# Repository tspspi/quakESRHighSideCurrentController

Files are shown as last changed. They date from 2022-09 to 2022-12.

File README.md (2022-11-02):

# Simple 500 mA high voltage biasable current source

This project contains a simple OpAmp and MosFET based current supply
that can be controlled using a serial port. The whole project is built
around an ```IRF540N``` MosFET that's driven by an ```LM358``` OpAmp in a way
to keep the voltage drop over a sense resistor constant - thus it provides
a controllable current source (note that there is no temperature compensation
but that was not necessary for this application).

The reference voltage is provided by an ```MCP4822``` SPI digital to analog
converter that's controlled by an ```ATMega328P```. The serial port that's used
to control the current source is isolated using two ```PC816``` optocouplers - this
is necessary since the whole board will be biased to ```-2 kV``` with respect to the
controlling system. The load is powered by an 12V isolation transformer, the controller
uses the same power supply and derives it's 5V supply for DAC and microcontroller using
a simple ```LM317``` linear voltage regulator.

## The schematic

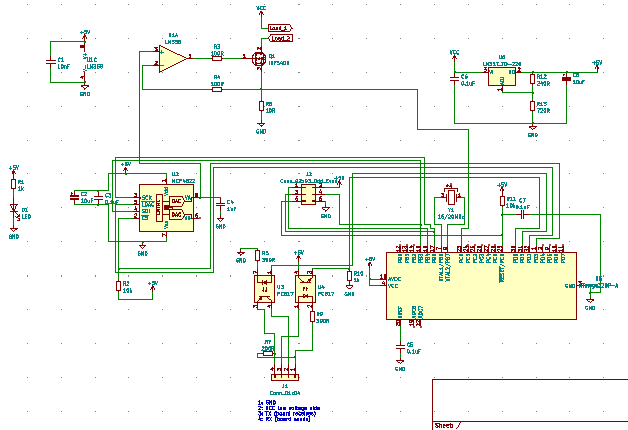
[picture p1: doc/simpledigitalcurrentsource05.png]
The schematic


The schematic can be found in KiCAD format in the ```/kicad/currentcontroller``` directory

## A PCB design

This repository includes also a simple PCB design

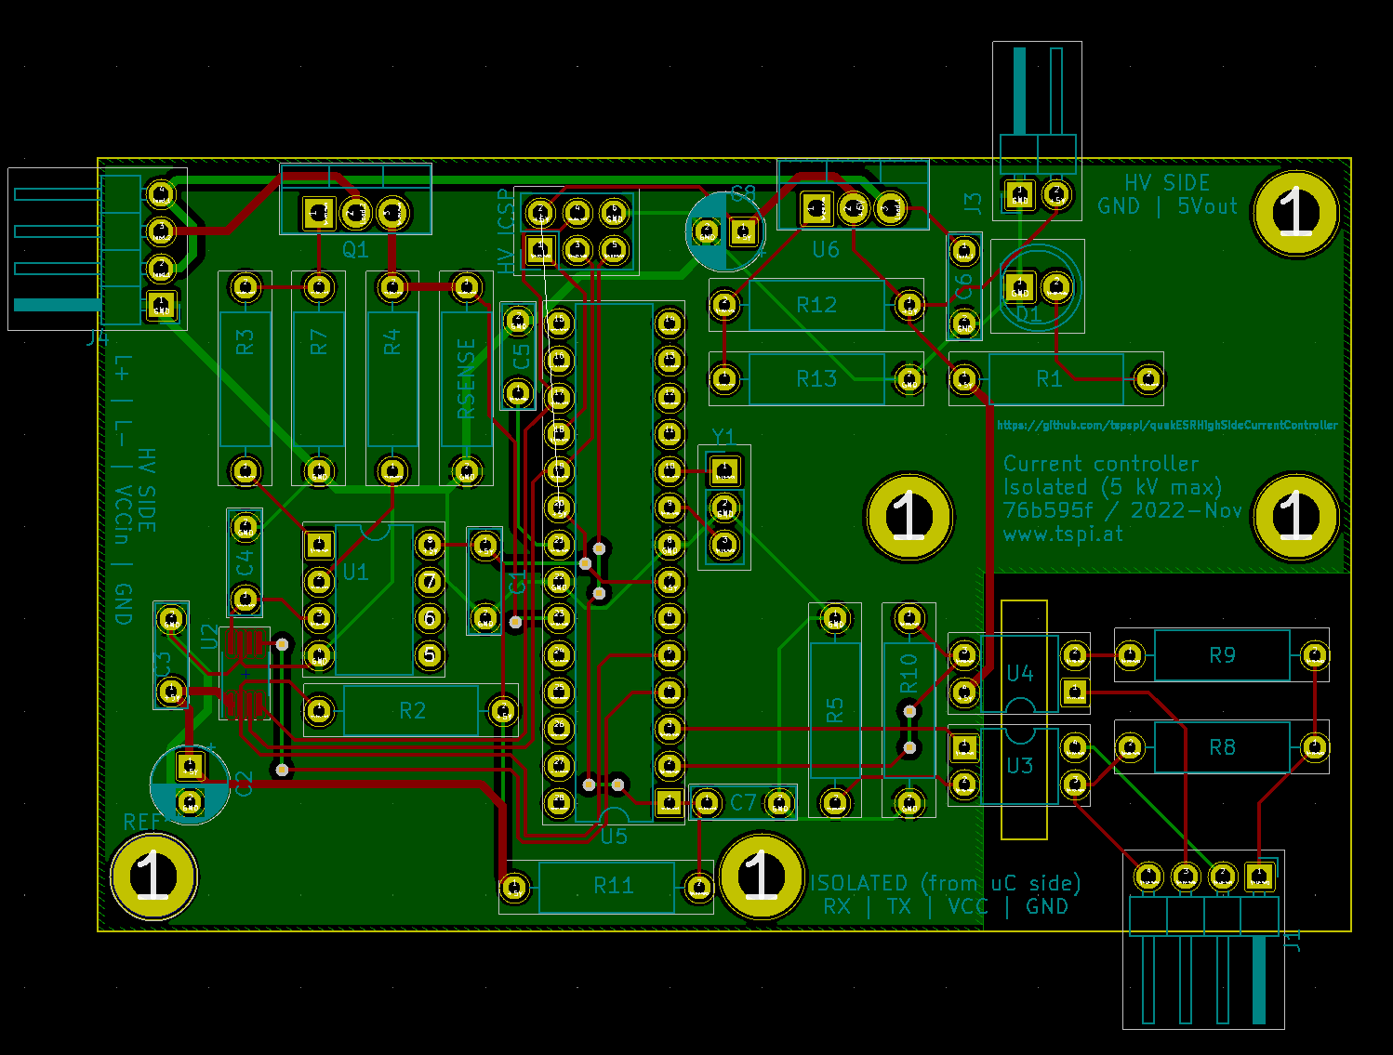
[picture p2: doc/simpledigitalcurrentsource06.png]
PCB design


## Microcontroller firmware

The firmware for the microcontroller can be found in ```mcusrc``` and is built
using ```avr-gcc```. The firmware can be flashed by using the ```Makefile```:

```
make flash
```

The ACSL annotations are work in progress.

## Test script

To test the communication using a [simple serial TTL to USB converter](https://amzn.to/3C0tQMZ)
a simple Python library is available (currently no PyPi package) at ```mcusrc/sertest```

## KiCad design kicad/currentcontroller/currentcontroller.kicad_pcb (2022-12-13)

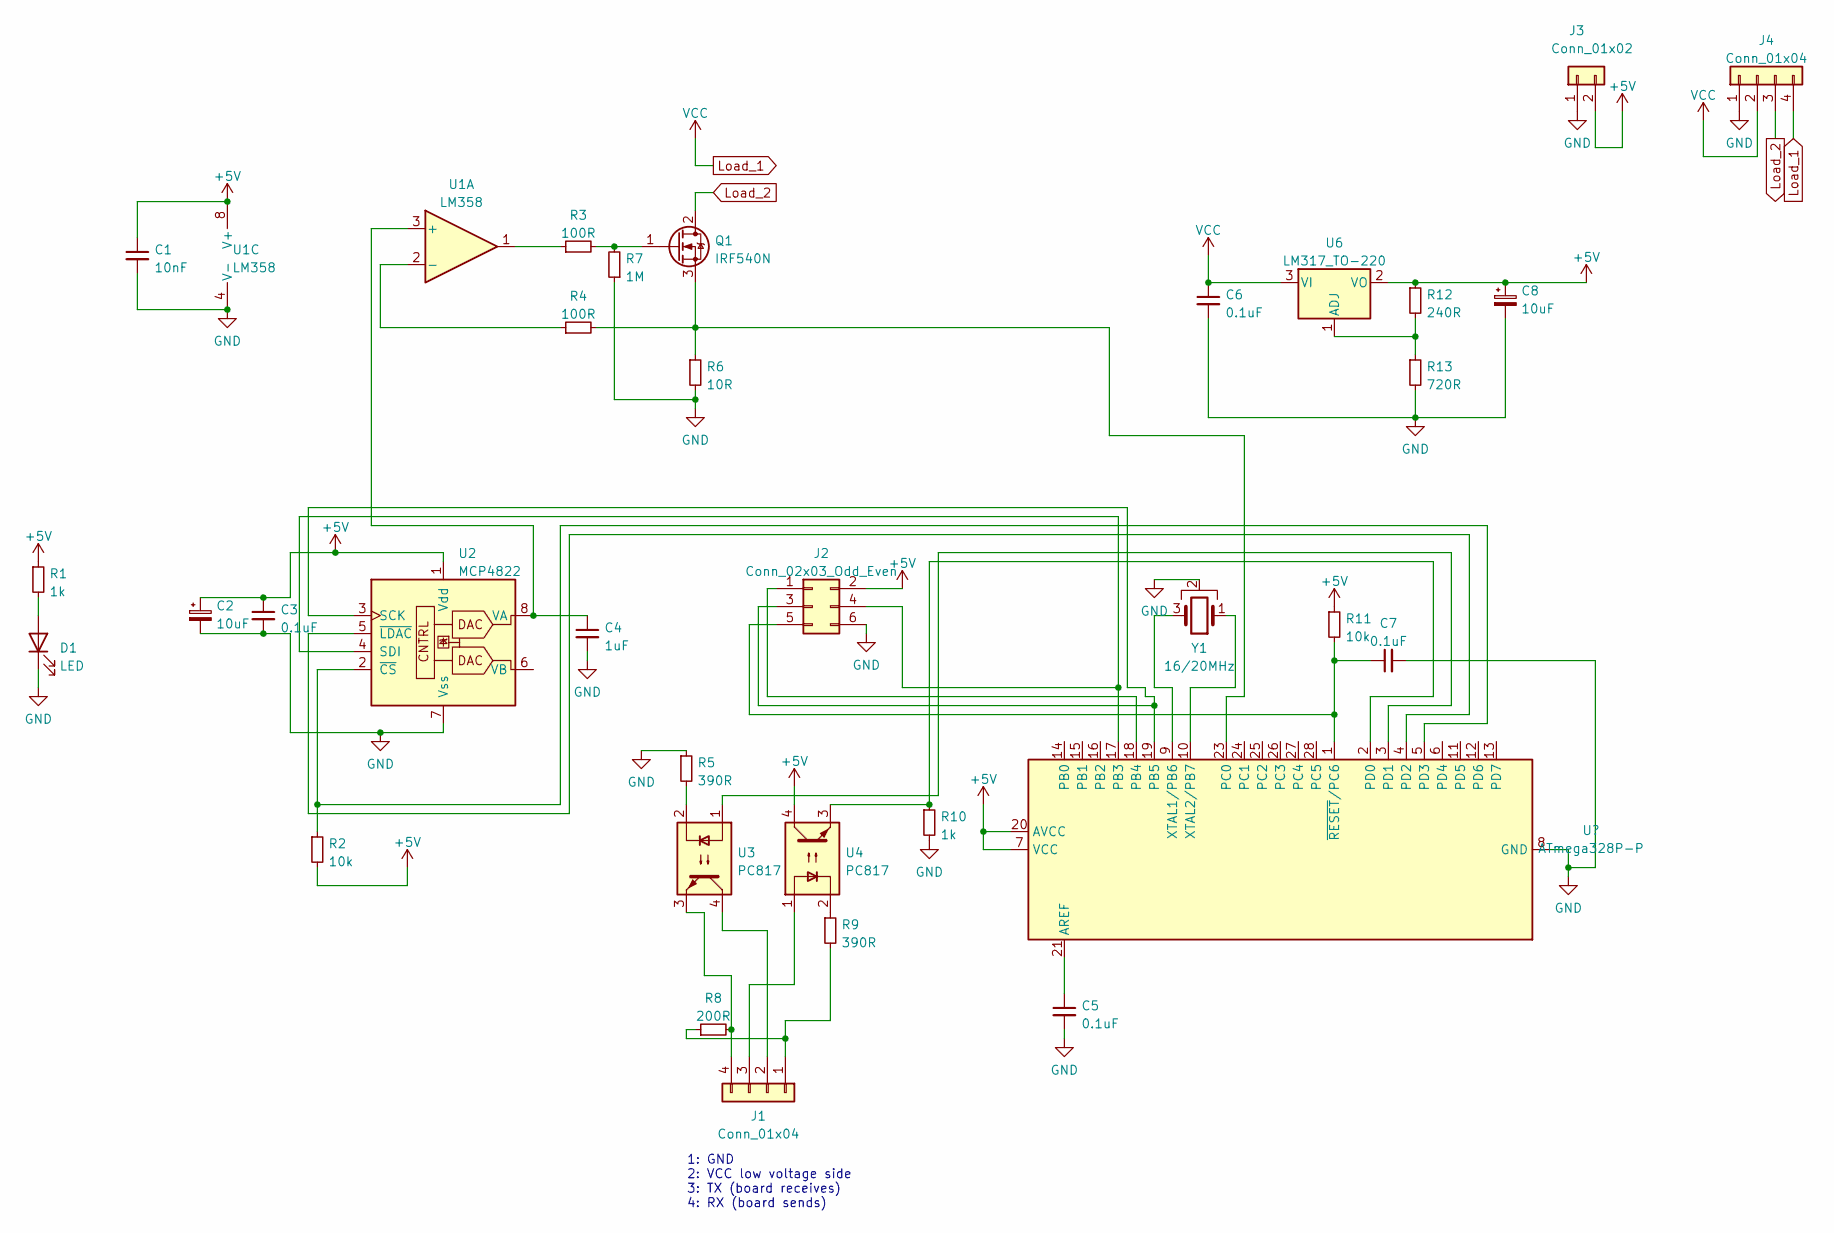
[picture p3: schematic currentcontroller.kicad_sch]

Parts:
C1: 10nF; C_Rect_L7.0mm_W2.0mm_P5.00mm
C2, C8: 10uF; CP_Radial_D5.0mm_P2.50mm
C3, C5, C6, C7: 0.1uF; C_Rect_L7.0mm_W2.0mm_P5.00mm
C4: 1uF; C_Rect_L7.0mm_W2.0mm_P5.00mm
D1: LED; LED_D5.0mm
J1, J4: Conn_01x04; PinHeader_1x04_P2.54mm_Horizontal
J2: Conn_02x03_Odd_Even; PinHeader_2x03_P2.54mm_Vertical
J3: Conn_01x02; PinHeader_1x02_P2.54mm_Horizontal
Q1: IRF540N; TO-220-3_Vertical
R1, R10: 1k; R_Axial_DIN0309_L9.0mm_D3.2mm_P12.70mm_Horizontal
R2, R11: 10k; R_Axial_DIN0309_L9.0mm_D3.2mm_P12.70mm_Horizontal
R3, R4: 100R; R_Axial_DIN0309_L9.0mm_D3.2mm_P12.70mm_Horizontal
R5, R9: 390R; R_Axial_DIN0309_L9.0mm_D3.2mm_P12.70mm_Horizontal
R6: 10R; R_Axial_DIN0309_L9.0mm_D3.2mm_P12.70mm_Horizontal
R7: 1M; R_Axial_DIN0309_L9.0mm_D3.2mm_P12.70mm_Horizontal
R8: 200R; R_Axial_DIN0309_L9.0mm_D3.2mm_P12.70mm_Horizontal
R12: 240R; R_Axial_DIN0309_L9.0mm_D3.2mm_P12.70mm_Horizontal
R13: 720R; R_Axial_DIN0309_L9.0mm_D3.2mm_P12.70mm_Horizontal
U1: LM358; DIP-8_W7.62mm
U2: MCP4822; MSOP-8_3x3mm_P0.65mm
U3, U4: PC817; DIP-4_W7.62mm
U6: LM317_TO-220; TO-220-3_Vertical
Y1: 16/20MHz; PinHeader_1x03_P2.54mm_Vertical

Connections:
+5V: C1.1, C2.1, C3.1, C8.1, J2.2, J3.2, R1.1, R2.2, R11.1, R12.1, U1.8 (V+), U2.1 (Vdd), U4.4, U6.2 (VO); also elsewhere on the board
GND: C1.2, C2.2, C3.2, C4.2, C5.2, C6.2, C7.2, C8.2, D1.1 (K), J2.6, J3.1, J4.1, R5.1, R6.2, R7.1, R10.2, R13.2, U1.4 (V-), U2.7 (Vss), Y1.2; also elsewhere on the board
Load_1: C6.1, J4.2, J4.4, U6.3 (VI)
Load_2: J4.3, Q1.2 (D)
unnamed: C4.1, U1.3 (+), U2.8 (VA)
unnamed 5: C5.1; also elsewhere on the board
unnamed 6: C7.1, J2.5, R11.2; also elsewhere on the board
unnamed: D1.2 (A), R1.2
unnamed: J1.1, R8.1, R9.2
unnamed: J1.2, U3.4
unnamed: J1.3, U4.1
unnamed: J1.4, R8.2, U3.3
unnamed 13: J2.3, U2.3 (SCK); also elsewhere on the board
unnamed 14: J2.4, U2.4 (SDI); also elsewhere on the board
unnamed: Q1.1 (G), R3.2, R7.2
unnamed 16: Q1.3 (S), R4.2, R6.1; also elsewhere on the board
unnamed 17: R2.1, U2.2 (~CS); also elsewhere on the board
unnamed: R3.1, U1.1
unnamed: R4.1, U1.2 (-)
unnamed: R5.2, U3.2
unnamed: R9.1, U4.2
unnamed 22: R10.1, U4.3; also elsewhere on the board
unnamed: R12.2, R13.1, U6.1 (ADJ)
unnamed 24: U2.5 (~LDAC); also elsewhere on the board
unnamed 25: U3.1; also elsewhere on the board
unnamed 26: Y1.1; also elsewhere on the board
unnamed 27: Y1.3; also elsewhere on the board

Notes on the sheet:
1: GND 2: VCC low voltage side 3: TX (board receives) 4: RX (board sends)

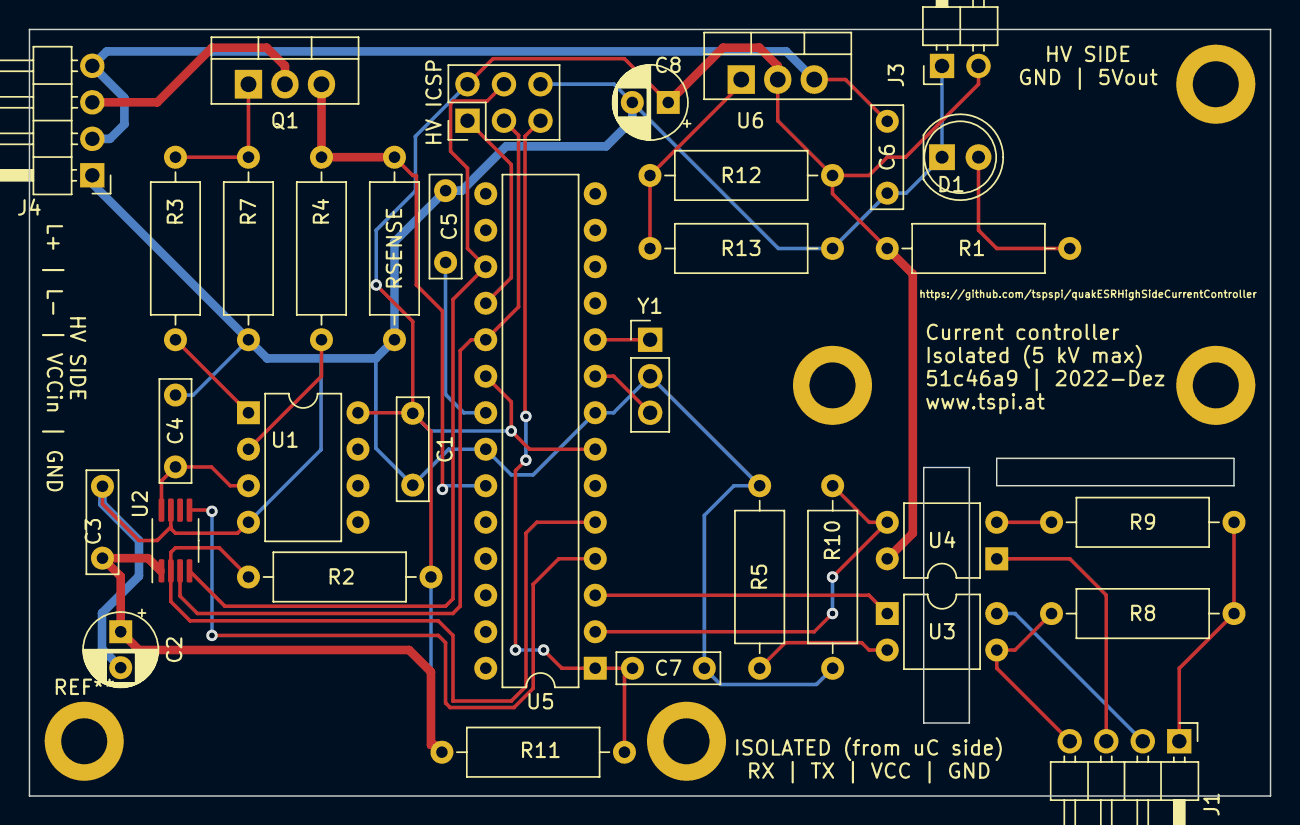
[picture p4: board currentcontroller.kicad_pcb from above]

Board: 2 copper layers, 86.4 x 53.3 mm, 34 parts (0 on the bottom side), 28 nets.

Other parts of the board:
HV ICSP: Conn_02x03_Odd_Even; PinHeader_2x03_P2.54mm_Vertical
RSENSE: 10R; R_Axial_DIN0309_L9.0mm_D3.2mm_P12.70mm_Horizontal
U5: ATmega328P-P; DIP-28_W7.62mm

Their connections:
+5V: HV ICSP.2, U5.7 (VCC), U5.20 (AVCC); also elsewhere on the board
GND: HV ICSP.6, RSENSE.2, U5.8 (GND), U5.22 (GND); also elsewhere on the board
unnamed 5: U5.21 (AREF); also elsewhere on the board
unnamed 6: HV ICSP.5, U5.1 (~RESET/PC6); also elsewhere on the board
unnamed: HV ICSP.1, U5.18 (PB4)
unnamed 13: HV ICSP.3, U5.19 (PB5); also elsewhere on the board
unnamed 14: HV ICSP.4, U5.17 (PB3); also elsewhere on the board
unnamed 16: RSENSE.1, U5.23 (PC0); also elsewhere on the board
unnamed 17: U5.5 (PD3); also elsewhere on the board
unnamed 22: U5.2 (PD0); also elsewhere on the board
unnamed 24: U5.4 (PD2); also elsewhere on the board
unnamed 25: U5.3 (PD1); also elsewhere on the board
unnamed 26: U5.10 (XTAL2/PB7); also elsewhere on the board
unnamed 27: U5.9 (XTAL1/PB6); also elsewhere on the board

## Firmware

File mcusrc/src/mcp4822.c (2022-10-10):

#define __is_in_module__142e0c51_431e_11ed_9e74_b499badf00a1 1

#include <avr/io.h>
#include <avr/interrupt.h>
#include <math.h>

#include "main.h"
#include "mcp4822.h"

#ifdef __cplusplus
	extern "C" {
#endif

uint16_t mcp4822_CurrentValues[2] = { 0, 0 };

/*@
	requires \valid(&SPCR) && \valid(&SPSR) && \valid(&PORTD);

	assigns PORTD;
	assigns SPCR;
	assigns SPSR;

	ensures (PORTD & 0x08) == 0;
	ensures SPCR == 0x53;
	ensures SPSR == 0x01;
*/
static inline void mcp4822SPI_TransferBegin() {
	SPCR = 0x50 | 0x03;
	SPSR = 0x01;

	/* Chip select to low ... */
	PORTD = PORTD & (~(0x08));
}
/*@
	requires \valid(&SPCR) && \valid(&PORTD);

	assigns PORTD;
	assigns SPCR;

	ensures (PORTD & 0x08) == 0x08;
	ensures SPCR == 0x40;
*/
static inline void mcp4822SPI_TransferEnd() {
	SPCR = 0x40;
	PORTD = PORTD | 0x08;
}
/*@
	requires \valid(&SPDR) && \valid(&SPSR);

	assigns SPDR;

	ensures \result == SPDR;
*/
static inline uint8_t mcp4822SPI_Transfer(uint8_t byteOut) {
	SPDR = byteOut;
	asm volatile("nop");
	while((SPSR & 0x80) == 0) { }
	return SPDR;
}
/*@
	requires \valid(&PORTD);

	assigns PORTD;

	ensures (PORTD & 0x04) == 0x04;
*/
static inline void mcp4822SPI_LatchOutputs() {
	PORTD = PORTD & (~0x04);
	/* Two NOPs to reach 100 ns minimum time (at 16 MHz each is ~ 62 ns) */
	//@ assert (PORTD & 0x04) == 0;
	asm volatile("nop");
	asm volatile("nop");
	PORTD = PORTD | 0x04;
}

/*@
	requires \valid(&SREG) && \valid(&DDRD) && \valid(&PORTD) && \valid(&DDRB) && \valid(&SPCR) && \valid(&SPSR);

	assigns SREG;
	assigns DDRD, PORTD;
	assigns DDRB;
	assigns SPCR, SPSR;
	assigns PRR;

	ensures (DDRD & 0x0C) == 0x0C;
	ensures (PORTD & 0x0C) == 0x0C;
	ensures ((DDRB & 0x24) == 0x24) && ((DDRB & 0x10) == 0);
	ensures (SPCR = 0x40) && (SPSR == 0x01);
	ensures SREG == \old(SREG);
	ensures PRR & 0x04 == 0x00;
*/
void mcp4822Init() {
	uint8_t sregOld = SREG;
	#ifndef FRAMAC_SKIP
		cli();
	#endif

	/*
		Set I/O pins for SPI
			PD3 -> nCS
			PD2 -> nLDAC
			PB5 -> SCK
			PB3 -> SDI (MOSI)
			PB4 -> MISO

			PB2 is slave select, should be configured as output

		nCS -> output, high
		nLDAC -> output, high

	*/
	DDRD = DDRD | 0x0C;
	PORTD = PORTD | 0x0C;
	DDRB = (DDRB | 0x2C) & (~(0x10));
	PORTB = PORTB | 0x2C;

	/* Disable power saving mode ... */
	PRR = PRR & ~(0x04);

	/* SPI master mode, enable logic */
	SPCR = 0x40;
	SPSR = 0x01;

	SREG = sregOld;

	/* Set our output values to 0 */
	mcp4822SetOutput(0, 0, false, 0);
	mcp4822SetOutput(1, 0, false, 0);
}

/*@
	requires (channel == 1) || (channel == 0);
	requires (gain == 1) || (gain == 0);
	requires (enableOutput == true) || (enableOutput == false);
	requires (value > 0) && (value < 4096);

	assigns SPSR, SPCR, SPDR;
	assigns mcp4822_CurrentValues[0], mcp4822_CurrentValues[1];

	ensures mcp4822_CurrentValues[channel] == value;
*/
void mcp4822SetOutput(
	uint8_t channel,
	uint8_t gain,
	bool enableOutput,
	uint16_t value
) {
	uint16_t msg = 0x00;

	/* Prepare message */
	msg = (value & 0x0FFF);
	if(channel != 0) {
		msg = msg | 0x8000;
	}
	if(gain != 0) {
		msg = msg | 0x2000;
	}
	if(enableOutput == true) {
		msg = msg | 0x1000;
	}

	/* Transmit 2 bytes ...*/
	mcp4822SPI_TransferBegin();
	mcp4822SPI_Transfer((uint8_t)((msg & 0xFF00) >> 8));
	mcp4822SPI_Transfer((uint8_t)(msg & 0x00FF));
	mcp4822SPI_TransferEnd();
	mcp4822SPI_LatchOutputs();

	mcp4822_CurrentValues[channel] = value;
}

#ifdef __cplusplus
	} /* extern "C" { */
#endif

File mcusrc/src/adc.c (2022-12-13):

#include <avr/io.h>
#include <avr/interrupt.h>
#include <avr/eeprom.h>
#include <math.h>
#include <util/twi.h>
#include <stdint.h>

#define CURRENT_MEASURE_ADC 0

#include "./adc.h"
#include "./main.h"

#ifdef __cplusplus
    extern "C" {
#endif

uint16_t currentADC[ADCCOUNT];

static double adcCal_K, adcCal_D;
static uint16_t adcCalLow_Counts;
static uint16_t adcCalHigh_Counts;
static uint16_t adcCalHigh_Milliamps;

/*@
	requires \valid(&ADC) && \valid(&ADMUX);

	assigns currentADC[0 .. ADCCOUNT];
*/
ISR(ADC_vect) {
	uint8_t oldMUX = ADMUX;
    currentADC[(oldMUX + (ADCCOUNT-1)) % ADCCOUNT] = ADC;
    ADMUX = (((oldMUX & 0x1F) + 1) % ADCCOUNT) | (oldMUX & 0xE0);
}

struct eepromCalData {
    double adc0_K;
    double adc0_D;

    uint8_t chkSum;
};

/*@
	requires \valid(&ADMUX) && \valid(&ADCSRB) && \valid(&ADCSRA) && \valid(&SREG);

    assigns ADMUX;
    assigns ADCSRB;
    assigns ADCSRA;
    assigns SREG;

    ensures (ADMUX == 0x40);
    ensures (ADCSRB == 0x00);
    ensures ADCSRA == 0xFF;
	ensures SREG == \old(SREG);
*/
void adcInit() {
    unsigned long int i;
    struct eepromCalData calData;

    uint8_t oldSREG = SREG;
    #ifndef FRAMAC_SKIP
        cli();
    #endif

    for(i = 0; i < sizeof(currentADC) / sizeof(uint16_t); i=i+1) {
        currentADC[i] = ~0;
    }

    ADMUX = 0x40; /* AVCC reference voltage, MUX 0, right aligned */
    ADCSRB = 0x00; /* Free running trigger mode, highest mux bit 0 */
    ADCSRA = 0xBF; /* Prescaler / 128 -> about 1 kHz measurement interrupt enable; ADCs currently DISABLED */

    SREG = oldSREG;

    /* Launch ADC ... */
    ADCSRA = ADCSRA | 0x40; /* Start first conversion ... */

    /*
        Load calibration data (if exists)...
    */
    eeprom_read_block(&calData, EEPROM_ADCCALDATAOFFSET, sizeof(struct eepromCalData));
    uint8_t chkSum = 0;
    for(i = 0; i < sizeof(struct eepromCalData); i=i+1) {
        chkSum = chkSum ^ ((uint8_t*)(&calData))[i];
    }
    if(chkSum == 0) {
        adcCal_D = calData.adc0_D;
        adcCal_K = calData.adc0_K;
    } else {
        adcCal_D = 0;
        adcCal_K = 0.522448979592;
    }
}



uint16_t adcCountsToCurrentMA() {
    uint16_t a;
    /*
        Apply our calibration curve ... currently in code, this should be stored in EEPROM ...
    */
    uint8_t sregOld = SREG;
    #ifndef FRAMAC_SKIP
        cli();
    #endif
    a = currentADC[CURRENT_MEASURE_ADC];
    SREG = sregOld;

    return (uint16_t)(((double)(a) * adcCal_K) + adcCal_D);
}

static void adcRecalculateKD() {
    if((adcCalHigh_Counts == adcCalLow_Counts) || (adcCalLow_Counts > adcCalHigh_Counts)) {
        /* Use some sane default values ... */
        adcCal_D = 0;
        adcCal_K = 0.522448979592;
    } else {
        adcCal_K = ((double)adcCalHigh_Milliamps) / ((double)adcCalHigh_Counts - (double)adcCalLow_Counts);
        adcCal_D = -1.0 * adcCal_K * ((double)adcCalLow_Counts);
    }
}

void adcCalLow() {
    uint8_t sregOld = SREG;
    #ifndef FRAMAC_SKIP
        cli();
    #endif
    adcCalLow_Counts = currentADC[CURRENT_MEASURE_ADC];
    SREG = sregOld;

    adcRecalculateKD();
}

void adcCalHigh(uint16_t milliAmps) {
    uint8_t sregOld = SREG;
    #ifndef FRAMAC_SKIP
        cli();
    #endif
    adcCalHigh_Counts = currentADC[CURRENT_MEASURE_ADC];
    adcCalHigh_Milliamps = milliAmps;
    SREG = sregOld;

    adcRecalculateKD();
}

void adcCalStore() {
    struct eepromCalData calData;
    calData.adc0_D = adcCal_D;
    calData.adc0_K = adcCal_K;
    calData.chkSum = 0;

    uint8_t chkSum = 0x00;
    unsigned long int i;
    for(i = 0; i < sizeof(struct eepromCalData); i=i+1) {
        chkSum = chkSum ^ ((uint8_t*)(&calData))[i];
    }
    calData.chkSum = chkSum;

    eeprom_write_block(&calData, EEPROM_ADCCALDATAOFFSET, sizeof(struct eepromCalData));
}

double adcCalGet_K() { return adcCal_K; }
double adcCalGet_D() { return adcCal_D; }

#ifdef __cplusplus
    } /* extern "C" { */
#endif

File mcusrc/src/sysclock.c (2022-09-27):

#include <avr/io.h>
#include <avr/interrupt.h>
#include <math.h>

#include "sysclock.h"

#ifdef __cplusplus
    extern "C" {
#endif

/*
    ================
    = System clock =
    ================
*/

#define SYSCLK_TIMER_OVERFLOW_MICROS                    (64L * 256L * (F_CPU / 1000000L))
#define SYSCLK_MILLI_INCREMENT                          (SYSCLK_TIMER_OVERFLOW_MICROS / 1000)
#define SYSCLK_MILLIFRACT_INCREMENT                     ((SYSCLK_TIMER_OVERFLOW_MICROS % 1000) >> 3)
#define SYSCLK_MILLIFRACT_MAXIMUM                       (1000 >> 3)

static volatile unsigned long int systemMillis                 = 0;
static volatile unsigned long int systemMilliFractional        = 0;
static volatile unsigned long int systemMonotonicOverflowCnt   = 0;
/*@
        axiomatic timerisr_has_valid_counters {
                axiom validMillis: (systemMillis >= 0) && (systemMillis < 4294967296);
                axiom validMillifracs: (systemMilliFractional >= 0) && (systemMilliFractional < 4294967296);
                axiom validOverflow: (systemMonotonicOverflowCnt >= 0) && (systemMonotonicOverflowCnt < 4294967296);
        }
*/

/*@
        requires (systemMillis >= 0) && (systemMillis < 4294967296);
        requires (systemMilliFractional >= 0) && (systemMilliFractional < 4294967296);
        requires (systemMonotonicOverflowCnt >= 0) && (systemMonotonicOverflowCnt < 4294967296);

        assigns systemMillis, systemMilliFractional, systemMonotonicOverflowCnt;

        ensures (systemMonotonicOverflowCnt == \old(systemMonotonicOverflowCnt)+1)
                || (systemMonotonicOverflowCnt == 0);

        ensures ((systemMillis == \old(systemMillis) + SYSCLK_MILLI_INCREMENT)
                && (systemMilliFractional == \old(systemMilliFractional + SYSCLK_MILLIFRACT_INCREMENT))
                && (\old(systemMilliFractional + SYSCLK_MILLIFRACT_INCREMENT < SYSCLK_MILLIFRACT_MAXIMUM)))
                ||
                ((systemMillis == \old(systemMillis) + SYSCLK_MILLI_INCREMENT + 1)
                && (systemMilliFractional == \old(systemMilliFractional + SYSCLK_MILLIFRACT_INCREMENT - SYSCLK_MILLIFRACT_MAXIMUM))
                && (\old(systemMilliFractional + SYSCLK_MILLIFRACT_INCREMENT >= SYSCLK_MILLIFRACT_MAXIMUM)));
*/
ISR(TIMER0_OVF_vect) {
        unsigned long int m, f;

        m = systemMillis;
        f = systemMilliFractional;

        m = m + SYSCLK_MILLI_INCREMENT;
        f = f + SYSCLK_MILLIFRACT_INCREMENT;

        if(f >= SYSCLK_MILLIFRACT_MAXIMUM) {
                f = f - SYSCLK_MILLIFRACT_MAXIMUM;
                m = m + 1;
        }

        systemMonotonicOverflowCnt = systemMonotonicOverflowCnt + 1;

        systemMillis = m;
        systemMilliFractional = f;
}

/*@
        assigns SREG;

        ensures (\result >= 0) && (\result < 4294967296);
        ensures SREG == \old(SREG);
*/
unsigned long int micros() {
        uint8_t srOld = SREG;
        unsigned long int overflowCounter;
        unsigned long int timerCounter;

        #ifndef FRAMAC_SKIP
                cli();
        #endif
        overflowCounter = systemMonotonicOverflowCnt;
        timerCounter = TCNT0;

        /*
                Check for pending overflow that has NOT been handeled up to now
        */
        if(((TIFR0 & 0x01) != 0) && (timerCounter < 255)) {
                overflowCounter = overflowCounter + 1;
        }

        SREG = srOld;

        return ((overflowCounter << 8) + timerCounter) * (64L / (F_CPU / 1000000L));
}

/*@
        requires millisecs > 0;

        assigns SREG;
*/
void delay(unsigned long millisecs) {
        unsigned int lastMicro, curMicro;
        /*
                Busy waiting the desired amount of milliseconds ... by
                polling mircos
        */
        lastMicro = (unsigned int)micros();
        //@ ghost int iterations = 0;
        /*@
                loop invariant millisecs >= 0;

                loop assigns SREG;
                loop assigns lastMicro, curMicro;

                loop variant millisecs - iterations;
        */
        while(millisecs > 0) {
                curMicro = micros();
                //@ ghost iterations = iterations + 1;
                if(curMicro - lastMicro >= 1000)  {
                        /* Every ~ thousand microseconds tick ... */
                        lastMicro = lastMicro + 1000;
                        millisecs = millisecs - 1;
                }
        }
        return;
}

/*@
        requires \valid(&TCCR0B) && \valid(&TCNT0) && \valid(&TCCR0A) && \valid(&TIFR0) && \valid(&TIMSK0) && \valid(&TCCR0B);
        requires \valid(&SREG);

        assigns TCCR0A;
        assigns TCNT0;
        assigns TCCR0A;
        assigns TIFR0;
        assigns TIMSK0;
        assigns TCCR0B;
        assigns SREG;

        assigns systemMillis, systemMilliFractional, systemMonotonicOverflowCnt;

        ensures TCCR0B == 0x00;
        ensures TCNT0  == 0x00;
        ensures TCCR0A == 0x00;
        ensures TIFR0  == 0x01;
        ensures TIMSK0 == 0x01;
        ensures TCCR0B == 0x03;
        ensures SREG == \old(SREG);

        ensures (systemMillis == 0) && (systemMilliFractional == 0) && (systemMonotonicOverflowCnt == 0);
*/
void sysclockInit() {
        uint8_t oldSr = SREG;
        #ifndef FRAMAC_SKIP
                cli();
        #endif

        systemMillis                 = 0;
        systemMilliFractional        = 0;
        systemMonotonicOverflowCnt   = 0;

        TCCR0B = 0x00;          /* Disable timer 0 */
        TCNT0  = 0x00;          /* Reset counter */

        TCCR0A = 0x00;
        TIFR0  = 0x01;          /* Clear overflow interrupt flag if triggered before */
        TIMSK0 = 0x01;          /* Enable overflow interrupt */
        TCCR0B = 0x03;          /* /64 prescaler */

        SREG = oldSr;
}

#ifdef __cplusplus
    } /* extern "C" { */
#endif

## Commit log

2022-09-27 Adjusted to other DAC
    [currentcontroller.kicad_sch]
2022-10-03 Added calibration curve for measurement
2022-10-03 Added configuration for current limit (software side) and EEPROM offsets
2022-10-03 Serial communication
    * Implemented disableable protection
    * Implemented setting and getting commands for current
    * Implemented measurement
    * Implemented calibration commands
2022-10-03 Reflecting latest changes on PCB
    [currentcontroller.kicad_sch]
2022-11-02 Minor updates and finished PCB
    [currentcontroller.kicad_pcb, currentcontroller.kicad_sch]
2022-11-02 Added images of schematic and PCB
2022-11-02 Added gerber files used for PCBWay
2022-12-12 Ability to simply define which channel to use for current measurement
2022-12-13 Changed ADC back to channel 0 (for new board)
2022-12-13 Missing 5V trace
    [currentcontroller.kicad_pcb]
2022-12-13 Added commit ID
    * Added commit ID
    * Added a second slot for isolated island
    [currentcontroller.kicad_pcb]
